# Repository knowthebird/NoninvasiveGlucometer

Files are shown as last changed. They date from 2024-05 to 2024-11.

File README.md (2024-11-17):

## Design and Build An Accurate Noninvasive Glucometer

### Table of Contents
1. [Overview](#overview)
2. [Example Sensors  (Glucosans)](#example-sensors-glucosans)
3. [Testing Notes](#testing-notes)
4. [Resources and References](#resources-and-references)

## Overview
This was originally to host a competition to design and build the most accurate noninvasive glucometer sensor.  Despite some interest, there were no entries.  Instead, now it currently just hosts my designs.  

The $1750 set aside for prizes will be kept available as a fund for anyone interested in developing a noninvasive glucometer sensor. If you have an idea for a design and want to chat about it or request some support, or if you are interested in refining these designs, reach out to noninvasiveglucometer@gmail.com

The motivation for the competition and designs is to increase the information available to the general public on noninvasive sensors by evaluating the accuracy of different sensor designs and to provide all the information needed to recreate those designs freely.  This is in the hopes that in the near future there may be an affordable sensor which can reliably provide accurate readings, and reduce the pain, cost, and waste associated with typical glucometers.
 
The information provided here has not been evaluated by the Food and Drug Administration.  The information provided here is not intended to diagnose, treat, cure, or prevent any disease.

Please feel free to reach out to noninvasiveglucometer@gmail.com with any questions, suggestions, comments, or concerns.

## Example Sensors (Glucosans)
This repository contains example "Glucosans" for reference. These are various designs to approach the problem, and the succeses and failures of them will be shared. 

**Glucosan**
 * **G**lucometer
 * **L**ightweight
 * **U**niversal
 * **C**ost-effective
 * **O**pen **S**ource
 * **A**ccurate
 * **N**oninvasive

| Overview | Glucosan 1 | Glucosan 2 |
| :--------- | :-------- | :------- |
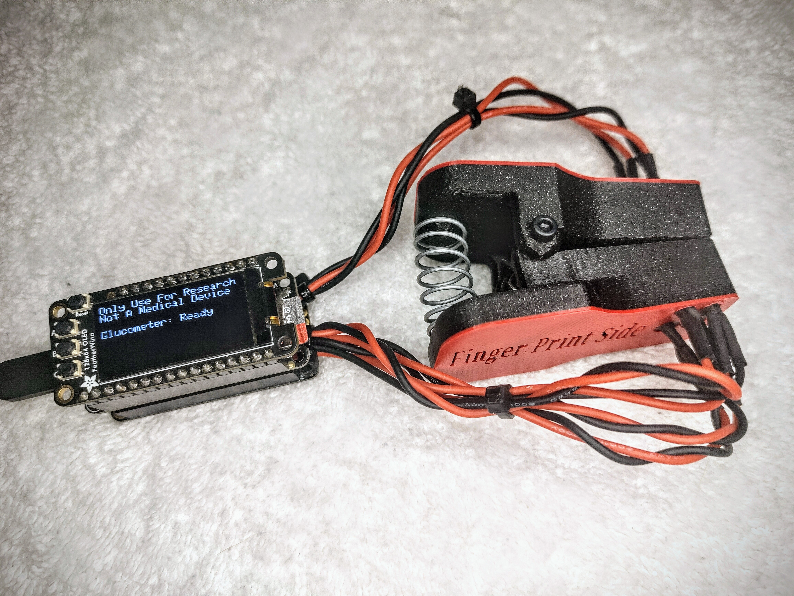
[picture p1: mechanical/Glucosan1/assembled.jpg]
| Image | | Coming Soon! |
| Method | IR Spectrometry | IR Spectrometry |
| Design | Done | In Progress |
| Build | Done | TODO |
| Log Data | 2 Persons, ~150 logs, 76-447mg/dl | TODO |
| Analysis Algorithims | External, Post Processing, Linear Regression | TODO |
| Correlations | Weak to None  | TODO |
| Emitters   | 1 x 617nm, 1 x 940nm | 1 x 670nm, 1 x 850nm, 1 x 950nm, 1 x 1300nm, 1 x 1550nm |
| Reflectance Detectors  | Phototransistors 1 x 630nm, 1 x 940nm (Si)  | None |
| Transmittance Detectors   | Phototransistors 1 x 630nm, 1 x 940nm (Si) | Photodiodes, 1 x 950nm (Si), 1 x 1650nm (InGaAs) |
| ADC | bypass caps, 12 bit resolution | analog front end IC, 14 bit resolution |
| Core Platform   | Adafruit Feather M0 Adalogger | Adafruit Feather RP2040 Adalogger |
| Display   | 128x64 OLED  | 128x64 OLED |
| SD Card   | CSV or Binary Logging | CSV or Binary Logging |
| Wireless   | None | None |
| IMU   | None  | 2 x Accel, 2 x Gyro |
| Temperature   | None  | 1 x Temp |
| Size   | TODO  | TODO |
| Weight   | TODO  | TODO |
| Power   | TODO  | TODO |
| Cost   | $48.33  | $188.31 |

## Testing Notes

<b>Nov 17, 2024:</b> Additional logs were taken with Glucosan 1 over a wide range of blood glucose levels. Looking closer at the log data showed what appeared to be corrupt signal readings, with a single sensor log showing multiple samples of the same photoplethysmogram (PPG) waveform slightly shifted. Because they were clearly shifted, but otherwise near identical signals representing the same PPG data, it does not look like an aliasing artifact from outside noise.  This can be seen looking at the readings from all sensors (regardless of LED state).  In some logs the corruption appears to "toggle" off and on, where the separation between duplicate signals widens.  My initial suspician is there is a hardware failure causing coupling between the sensors. It was not identified until reviewing a large set of samples. This should be kept in mind when referring to data from logs 85 to 174.  See log data folder for more details.

Initial tests with Glucosan 1 have showed weak to no correlation with blood glucose levels.  This is after gaining a wider range of data (see UserTwoLogData.csv) to verify outputs.  This may be due a few causes, including:
* Flexibility in the finger clamp was intended to allow a better seal on the finger from ambient light.  Distance of light source to sensor significantly affects readings.  Very possible changes in finger (emitter/sensor) positions are overshadowing any blood glucose levels changes detected by the sensor. Slightly moving the finger forward or backward in the clamp can almost immediatly exceed a .25V difference.  Possible solutions are puting the emitter and sensor in fixed positions where the clamp is not flexible, or including IMUs on the sensor and emitter such that the distance between the two can be calculated.
* Similarly, Nothing controlling movement, shaking, or vibrations when taking readings, or tracking them to filter against. A solution could be to use IMUs could monitor movement, or alert the user the device/finger is not stable enough to take a valid measurement. 
* Lack of environmental controls.  Glucosan 1 is portable and used in a variety of environments, and could be influenced by factors like various lighting. Possible solution is to always use in the same position for tests.

<b>July, 2024:</b> So far with Glucosan 1, only weak correlations have been observed.  This has relatively little significance at this point though, because it has only logged a very small amount of data with a relatively small range of blood glucose levels.  Getting a large set of samples, with a range in blood glucose levels, to both train and test models, is a challenge for any new sensor developemnt.  Without a range of data, initial results, such as MARD or RMSE, can be very misleading.
   * <b>YoutTube Video - Noninvasive Glucometer, Part 1, Initial Design Progress </b>
YoutTube Video, Noninvasive Glucometer, Part 1, Initial Design Progress (https://www.youtube.com/watch?v=Cop63ntB-sQ)

## Resources and References

1. Hina A, Saadeh W. Noninvasive Blood Glucose Monitoring Systems Using Near-Infrared Technology-A Review. Sensors (Basel). 2022 Jun 27;22(13):4855. doi: 10.3390/s22134855. PMID: 35808352; PMCID: PMC9268854.
   * https://www.mdpi.com/1424-8220/22/13/4855
2. Javid B, Fotouhi-Ghazvini F, Zakeri FS. Noninvasive Optical Diagnostic Techniques for Mobile Blood Glucose and Bilirubin Monitoring. J Med Signals Sens. 2018 Jul-Sep;8(3):125-139. doi: 10.4103/jmss.JMSS_8_18. PMID: 30181961; PMCID: PMC6116315.
   * https://pmc.ncbi.nlm.nih.gov/articles/PMC6116315/
3. Meter, G. (2015, August 27). Open Source Non-Invasive Glucose Meter - Expensive, Wasteful, and Annoying. YouTube
   * https://youtu.be/2np7Va2ASF0?si=skVRlG87lIETs9TL
4. Bhuyan, Muhibul. (2020). Design and Implementation of an NIR-Technique Based Non-Invasive Glucometer using Microcontroller. 20. 
   * https://tinyurl.com/j6b6d8wd
5. Beckers, I. (n.d.). Measuring glucose concentration nir absorption spectroscopy. Oxford Instruments. 
   * https://andor.oxinst.com/learning/view/article/spectral-response-of-glucose 
6. Naresh M, Nagaraju VS, Kollem S, Kumar J, Peddakrishna S. Non-invasive glucose prediction and classification using NIR technology with machine learning. Heliyon. 2024 Mar 28;10(7):e28720. doi: 10.1016/j.heliyon.2024.e28720. PMID: 38601525; PMCID: PMC11004754.
   * https://www.sciencedirect.com/science/article/pii/S2405844024047510

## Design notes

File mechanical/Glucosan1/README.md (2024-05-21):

FIngerClampBase.stl and FingerClampTop.stl modified from https://www.thingiverse.com/thing:2052975 by Drasko (https://www.thingiverse.com/drasko/designs). Original provided under the under the Creative Commons - Attribution license, CC BY, https://creativecommons.org/licenses/by/4.0/

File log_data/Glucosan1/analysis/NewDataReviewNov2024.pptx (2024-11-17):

## Noninvasive Glucometer

General Updates
Nov 2024
https://github.com/knowthebird/NoninvasiveGlucometer

## Contest Updates

- There were no contest entries
  - Prizes will be saved/used as fund for noninvasive glucometer projects
  - If you have an idea for a design and want to chat about it, or request some support, or if you are interested in refining the designs in the git repo, reach out to noninvasiveglucometer@gmail.com
- There were people who reached out with interest in how things were designed and suggestions for improvements in the future
- Just because there were not entries in the contest does not mean there is not interest in the problem
  - Many are going to look to protect their intellectual property, and not quickly share it for collaboration

## New Log Data

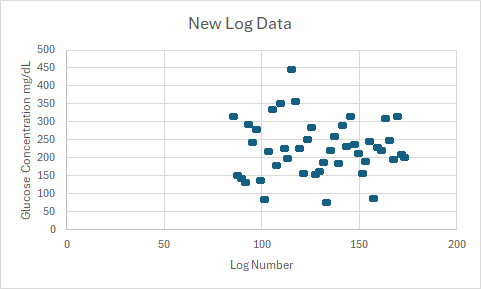
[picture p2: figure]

- Lots of new samples,
  - 89, two logs per session, separate fingers
  - A very wide range of concentration, 76 – 447 mg/dL
  - Thank you Dave!
- Expected results are:
  - As blood glucose concentration increases more light is absorbed by the glucose and both reflectance and transmittance sensors report less light
  - For this design, sensors report higher voltage when more light is absorbed
    - 12-bit resolution, 3V ~= 4096, 0V = 0
  - When looking at results, higher number should mean higher concentration
- This was not observed.
  - Even when looking at the same finger and same sensor, the general voltage does not follow the glucose concentration.

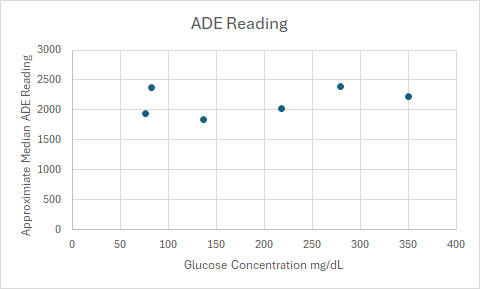
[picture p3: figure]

## Glucosan 1- Hardware Failure

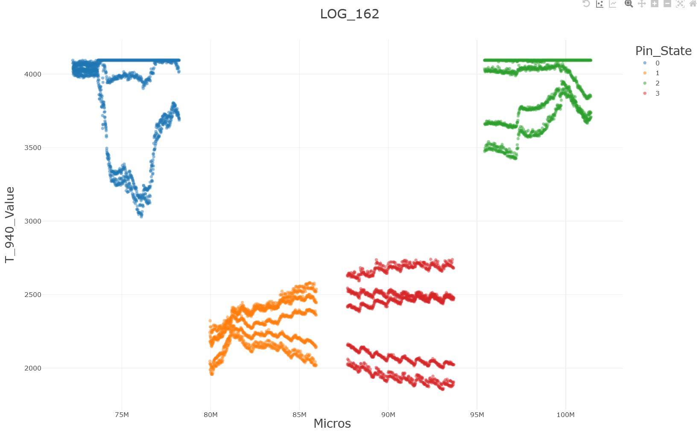
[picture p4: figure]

PPG Waveform appears to be
Duplicated in readings.

## Glucosan 1- Hardware Failure

Duplication appears to be present in
almost every log for 85-174. In some log
files it appeared to “toggle” off and on.
Note, there are not new software calls that
should be made during this “toggle”.

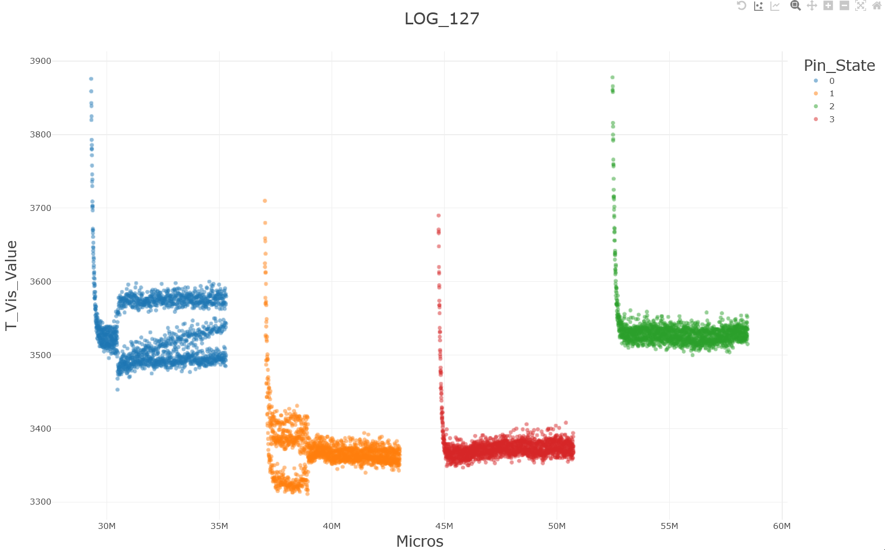
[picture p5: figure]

Signal appears to become duplicated .
Occurs in state where LEDs or all off.

Duplication appears to stop.
Occurs in state where one LEDs is on.

## Glucosan 1- Hardware Failure

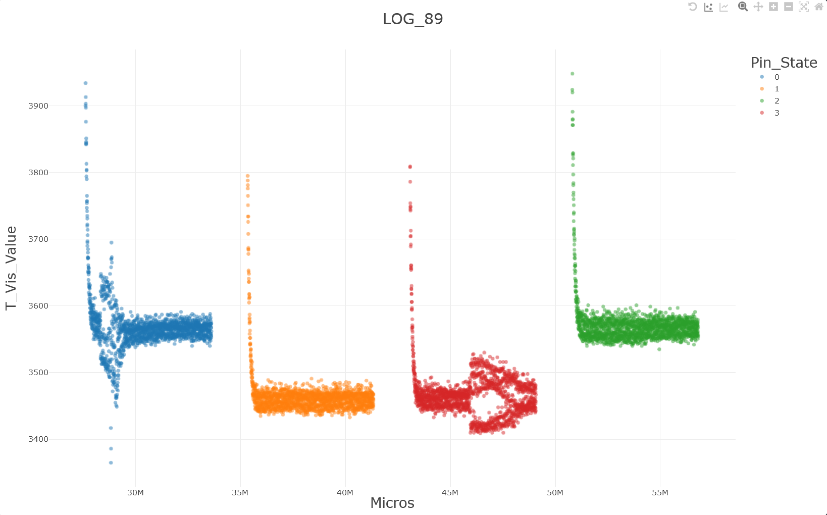
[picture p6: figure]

Even when less separated, there does appear
to be duplication or shifting occurring here.

Duplication becomes less seperated.
Occurs in state where LEDs or all off.

Duplication appears to widen again.
Occurs in state where two LEDs are on.

## Glucosan 1- Hardware Failure

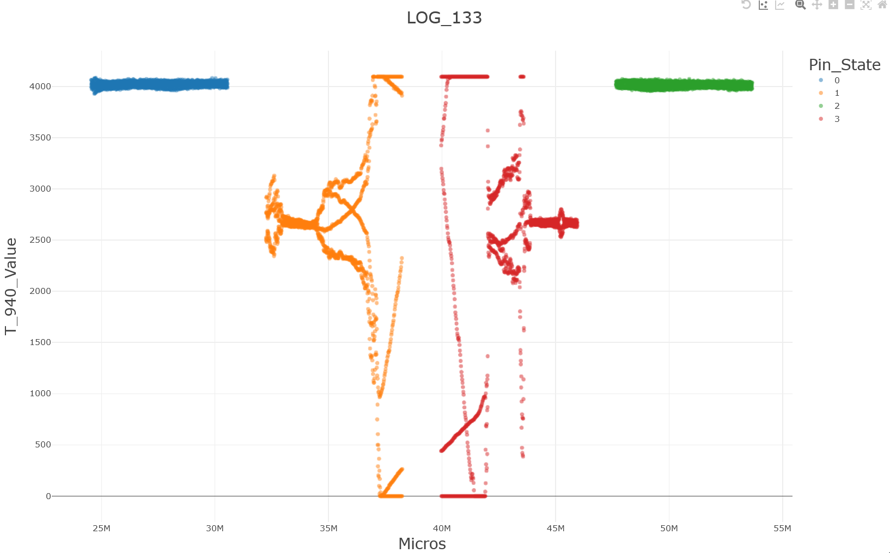
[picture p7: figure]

In some cases, the sensors appear to be completely failing.

## Movement Artifacts

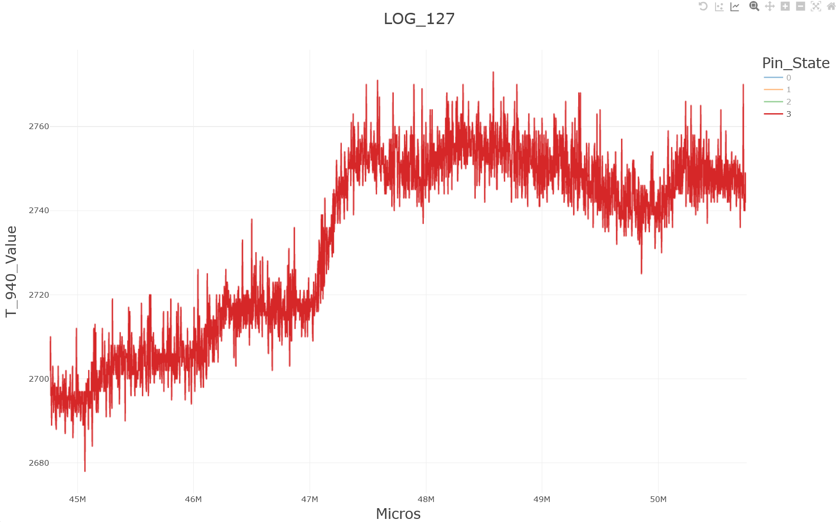
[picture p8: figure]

- Easy to see visually looking at logs but will require post processing algorithms to filter out.
- Currently no IMU to monitor for movement for post processing or to alert.

## In Hindsight – Lesson Learned

- Getting a variety of samples is not trivial
  - Glucose concentrations typically stays in a set range, and extremes are a health risk.
- Hardware needs to be more reliable before sending out in the world
- A way of sharing results remotely (ex: over wifi), could make it easier to remotely identify issues faster

## Short Term Next Steps – Simplify the Problem

- Measure Controlled Samples In A Controlled Environment
  - Cuvette containing solution of dextrose monohydrate in distilled water
  - Fixed position of emitters and sensors
    - Can 3D print a jig
  - PC Oscilloscope for Sampling Sensor
    - Built in Logging
      - No concerns of microcontroller wiring or logging corrupting sampling
    - High Sampling Rates
      - Will be more helpful when ready to monitor PPG waveforms
  - Test with probes and consider coverings to reduce noise in readings.

## Longer Term – Improvements For A Portable Device

- Fixed position for Sensor and Emitter
  - Makes problem less complex when not accounting for their movement
- IMUs on device and/or finger/ear
  - Need to be able to say what are artifacts of movement and be able to notify user of bad samples
- Maybe Cover the sensor and emitter
  - Maybe you a bag, glove, or cover of some kind to prevent noise on sensors
  - May be more important with a fixed sensor/emitter introducing air gaps
- Very long term, consider ability to share data through wifi or cell phone application
  - Could allow quicker results, and possibly a method for pushing updates back to the device
  - Adds complexity and data security risks too

## The Research and Development Is Active

- Companies
  - Abbott Laboratories
  - Apollon
  - Ascensia Diabetes Care Holdings AG
  - Biolinq Inc.
  - DexCom, Inc.
  - DiaMonTech AG
  - Glucosense Diagnostics
  - HagarTech
  - Integrity Applications, Inc.
  - Know Labs
  - LifePlusAI
  - LifeScan, Inc.
  - Medtronic plc
  - Movano, Inc.
  - Nemaura Medical
  - Profusa, Inc.
  - Roche Diagnostics
  - Scanbo
  - Senseonics Holdings, Inc.
  - RSP Systems
  - PK Vitality
  - Cnoga

Universities
Cardiff University
Kennesaw State University
Massachusetts Institute of Technology (MIT)
Monash University
National Taiwan Ocean University
RMIT University
Singapore National Population Health Survey
University of Chinese Academy of Sciences
University of Leeds
University of Missouri
Ulsan National Institute of Science and Technology (UNIST)

Lists provided by Amer Khaqan

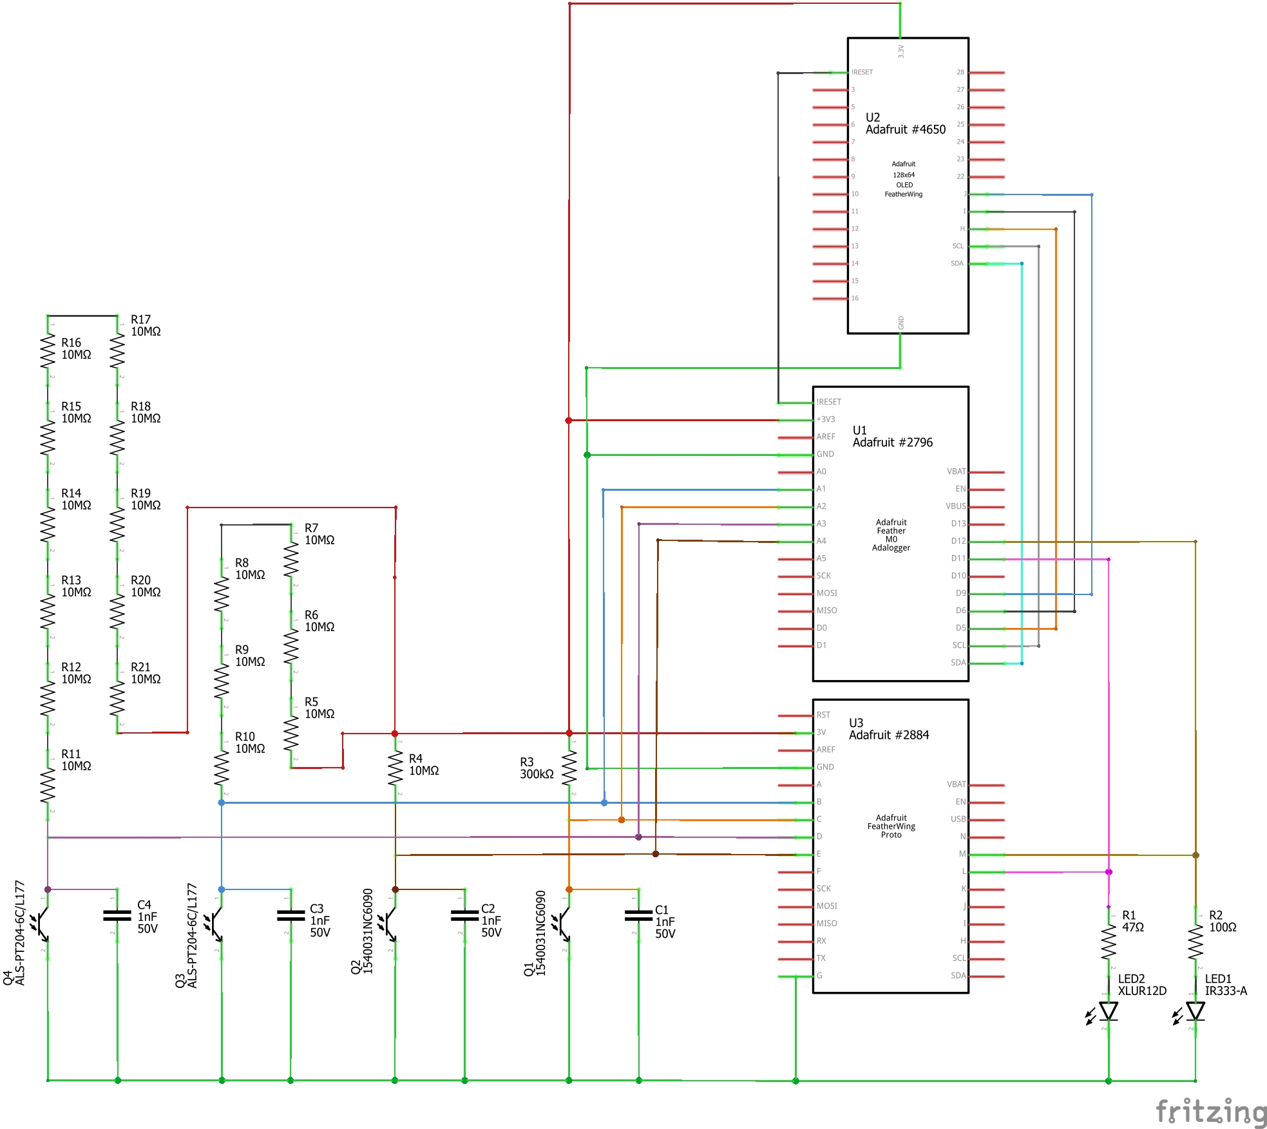
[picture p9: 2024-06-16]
electrical/Glucosan1/Schematic.jpg

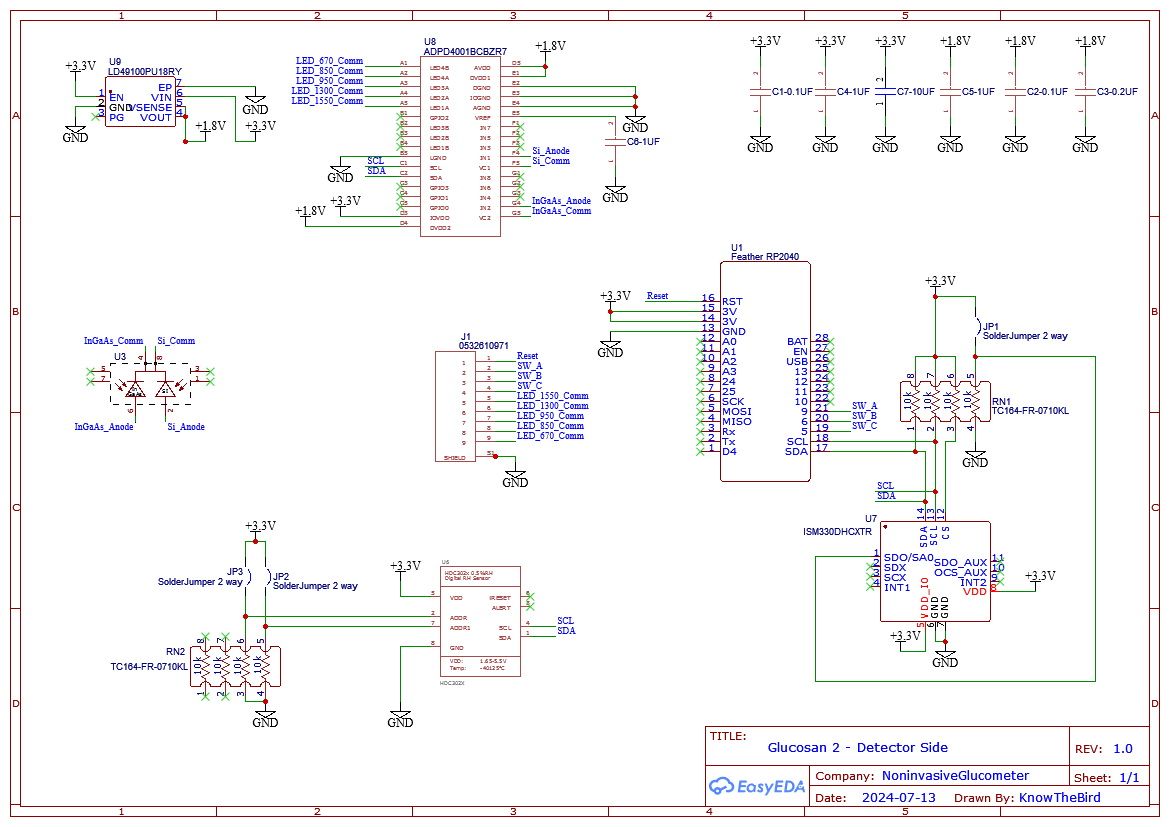
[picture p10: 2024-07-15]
electrical/Glucosan2/Schematic_Glucosan2-DetectorSide.png

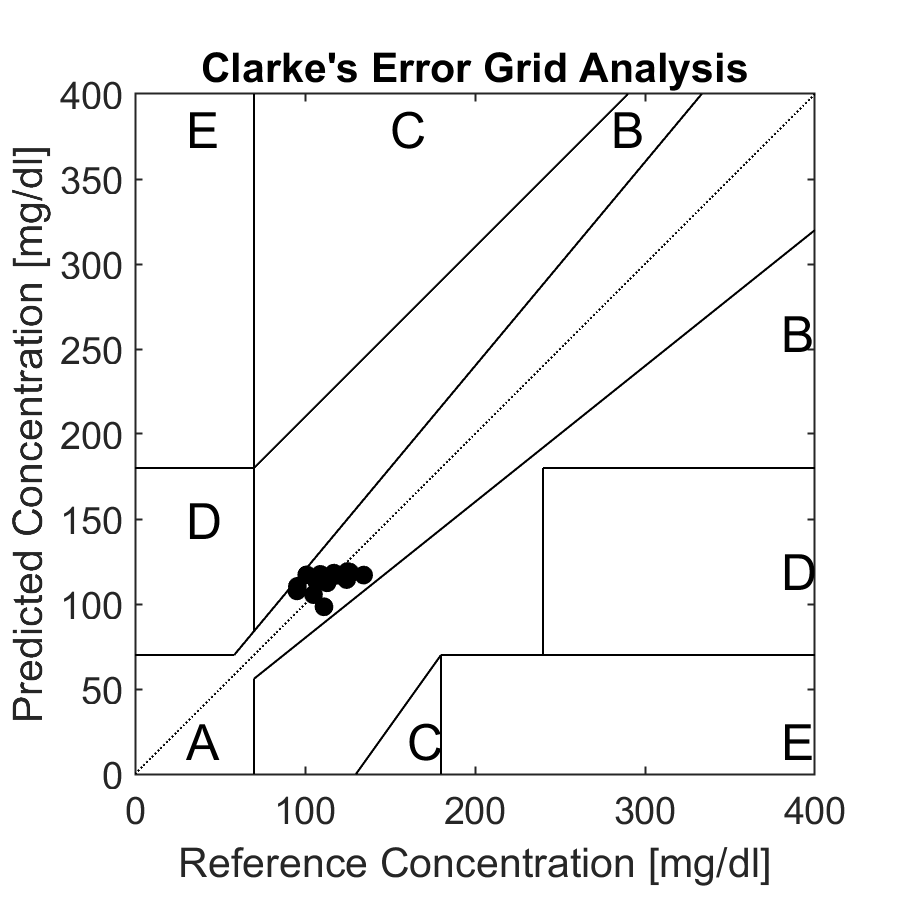
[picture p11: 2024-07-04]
log_data/Glucosan1/analysis/Clarke_EGA.png

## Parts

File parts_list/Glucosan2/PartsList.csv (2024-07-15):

Reference ID | Manufacturer or Supplier Part Number | Description | Manufacturer or Supplier | Quanity | Cost per Unit | Total Cost | Link
U1 | 5980 | Adafruit Feather RP2040 Adalogger | Adafruit | 1 | $14.95 | $14.95 | https://www.adafruit.com/product/5980
U2 | 4650 | FeatherWing 128x64 OLED | Adafruit | 1 | $14.95 | $14.95 | https://learn.adafruit.com/adafruit-128x64-oled-featherwing
U3 | MT03-047 | Photodiode 950/1650NM SMD | Marktech Optoelectronics | 1 | $55.36 | $55.36 | https://www.digikey.com/en/products/detail/marktech-optoelectronics/MT03-047/9954357
U4 | MTMD6891T38 | Emmiter IR MULTI-NM 100MA TO-5-8 | Marktech Optoelectronics | 1 | $40.68 | $40.68 | https://www.digikey.com/en/products/detail/marktech-optoelectronics/MTMD6891T38/4746379
U5 | MTE5115W-WRC | SWIR Emitter 1550NM TO-46 FLAT L | Marktech Optoelectronics | 1 | $15.32 | $15.32 | https://www.digikey.com/en/products/detail/marktech-optoelectronics/MTE5115W-WRC/9955415
U6 | HDC3021DEHR | Humidity Temperature Sensor Surface Mount I2C | Texas Instruments | 1 | $4.54 | $4.54 | https://www.digikey.com/en/products/detail/texas-instruments/HDC3021DEHR/17884945
U7 | ISM330DHCX | Accelerometer Gyroscope I2C | STmicroelectronics | 2 | $9.60 | $19.20 | https://www.st.com/en/mems-and-sensors/ism330dhcx.html#overview
U8 | ADPD4001BCBZR7 | Sensor Interface Multi-modal Optical AFE I2C | Analog Devices | 1 | $15.37 | $15.37 | https://www.mouser.com/ProductDetail/Analog-Devices/ADPD4001BCBZR7?qs=l4Gc20tDgJKpnSaEa3zOeQ%3D%3D
U9 | LD49100PU18RY | IC REG LINEAR 1.8V 1A 6DFN | STmicroelectronics | 1 | $1.61 | $1.61 | https://www.digikey.com/en/products/detail/stmicroelectronics/LD49100PU18RY/13175992
RN1 | TC164-FR-0710KL | 10k Resistor Array | Yageo | 2 | $0.14 | $0.28 | https://www.digikey.com/en/products/detail/yageo/TC164-FR-0710KL/5950695
C1-C3 | GCJ188R71E104KA12D | Capacitor ceramic 0.1uF 0603 | Murata Electronics | 3 | $0.17 | $0.51 | https://www.digikey.com/en/products/detail/murata-electronics/GCJ188R71E104KA12D/7363221
C4-C6 | GCJ188R71E105KA01D | Capacitor ceramic 1uF 0603 | Murata Electronics | 3 | $0.27 | $0.81 | https://www.digikey.com/en/products/detail/murata-electronics/GCJ188R71E105KA01D/6606038
C7 | CGA4J1X7S1E106K125AE | Capacitor ceramic 10uF 0805 | TDK Corporation | 1 | $0.73 | $0.73 | https://www.digikey.com/en/products/detail/tdk-corporation/CGA4J1X7S1E106K125AE/9744777
S1 | 2940 | 12-pin and 16-pin Female Header Set Short | Adafruit | 2 | $1.50 | $3.00 | https://www.adafruit.com/product/2940
S2 | 3002 | 12-pin and 16-pin Male Header Set Short | Adafruit | 2 | $0.50 | $1.00 | https://www.adafruit.com/product/3002
S3 | 532610971 | Connector Header SMD Right Angle 9 Pos PicoBlade | Molex | 2 | $1.01 | $2.02 | https://www.digikey.com/en/products/detail/molex/0532610971/699101
NA | 3096525-M | Wire Solder 180 C | MULTICORE / LOCTITE | As Needed | NA | NA | https://www.amazon.com/gp/product/B00DKF13JY/ref=ppx_yo_dt_b_search_asin_title?ie=UTF8&psc=1
 |  | Total |  |  |  | $190.33

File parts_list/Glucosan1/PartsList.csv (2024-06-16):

Reference ID | Manufacturer or Supplier Part Number | Description | Manufacturer or Supplier | Quanity | Cost per Unit | Total Cost | Link
U1 | 2796 | Adafruit Feather M0 Adalogger | Adafruit | 1 | $19.95 | $19.95 | https://learn.adafruit.com/adafruit-feather-m0-adalogger
U2 | 4650 | FeatherWing 128x64 OLED | Adafruit | 1 | $14.95 | $14.95 | https://learn.adafruit.com/adafruit-128x64-oled-featherwing
U3 | 2884 | FeatherWing Proto | Adafruit | 1 | $4.95 | $4.95 | https://www.adafruit.com/product/2884
P1 | 2830 | 12-pin and 16-pin Stacking Headers | Adafruit | 1 | $1.25 | $1.25 | https://www.adafruit.com/product/2830
S1 | 2886 | 12-pin and 16-pin Female Header Set | Adafruit | 1 | $0.95 | $0.95 | https://www.adafruit.com/product/2886
Q1-Q2 | 1540031NC6090 | Phototransistors 940nm | Würth Elektronik | 2 | $0.44 | $0.88 | https://www.digikey.com/en/products/detail/w%C3%BCrth-elektronik/1540031NC6090/12366941
Q3-Q4 | ALS-PT204-6C/L177 | Phototransistors 630nm Radial | Everlight Electronics Co Ltd | 2 | $0.62 | $1.24 | https://www.digikey.com/en/products/detail/everlight-electronics-co-ltd/ALS-PT204-6C-L177/2675510
LED1 | IR333-A | EMITTER IR 940NM 100MA RADIAL | Everlight Electronics Co Ltd | 1 | $0.53 | $0.53 | https://www.digikey.com/en/products/detail/everlight-electronics-co-ltd/IR333-A/2675571
LED2 | XLUR12D | Red 617nm LED Indication | SunLED | 1 | $0.28 | $0.28 | https://www.digikey.com/en/products/detail/sunled/XLUR12D/4745846
R1 | CF14JT47R0 | Resistor 47 Ohm 1/4 Watt 5% Tolerance Through Hole | Stackpole Electronics Inc | 1 | $0.10 | $0.10 | https://www.digikey.com/en/products/detail/stackpole-electronics-inc/CF14JT47R0/1741438
R2 | CF14JT100R | Resistor 100 Ohm 1/4 Watt 5% Tolerance Through Hole | Stackpole Electronics Inc | 1 | $0.10 | $0.10 | https://www.digikey.com/en/products/detail/stackpole-electronics-inc/CF14JT100R/1741261
R3 | CF14JT300K | Resistor 300k Ohm 1/4 Watt 5% Tolerance Through Hole | Stackpole Electronics Inc | 1 | $0.10 | $0.10 | https://www.digikey.com/en/products/detail/stackpole-electronics-inc/CF14JT300K/1741393
R4-R21 | An-resistor01 | Resistor 10M Ohm 1/4 Watt 1% Tolerance Through Hole | Aniann | 18 | $0.01 | $0.18 | https://www.amazon.com/dp/B07L851T3V?psc=1&ref=ppx_yo2ov_dt_b_product_details
C1-C4 | EE916A | Capacitor 1nF Ceramic 50V Radial Lead | 1A Manufacturing Ltd. | 4 | $0.10 | $0.40 | https://www.amazon.com/dp/B094HRK8QX?ref=ppx_yo2ov_dt_b_product_details&th=1
SPR1 | 540278 | Spring Compression #93 1.125" long 0.5"od .287mm solid height 5lbs per in | HILLMAN | 1 | $1.99 | $1.99 | https://shop.hillmangroup.com/ccrz__ProductDetails?sku=540278&cclcl=en_US/1000
CS1-CS2 | 91290A120 | Screw M3 x 16mm Socket Head Steel Black Oxide | McMASTER | 2 | $0.12 | $0.24 | https://www.mcmaster.com/91290A120/
HN1-HN2 | 90593A001 | Nut M3 Hex Steel Black Oxide | McMASTER | 2 | $0.12 | $0.24 | https://www.mcmaster.com/90593A001/
NA | 22GA | 22 AWG Stranded Wire Kit (multicolor) Silicone Coated | WiderCable | As Needed | NA | NA | https://www.amazon.com/gp/product/B07T4SYVYG/ref=ppx_yo_dt_b_search_asin_title?ie=UTF8&th=1
NA | 3096525-M | Wire Solder 180 C | MULTICORE / LOCTITE | As Needed | NA | NA | https://www.amazon.com/gp/product/B00DKF13JY/ref=ppx_yo_dt_b_search_asin_title?ie=UTF8&psc=1
NA | MP-H002-04-156 | Heat Shrink Tubing Kit Assorted Sizes | MILAPEAK | As Needed | NA | NA | https://www.amazon.com/gp/product/B07QM8249H/ref=ppx_yo_dt_b_search_asin_title?ie=UTF8&psc=1
NA | 4+6+8+12 (400 Pack) | Wire Ties Assorted Sizes UV Resistant | ANOSON | As Needed | NA | NA | https://www.amazon.com/gp/product/B0C2Z4L3S6/ref=ppx_yo_dt_b_search_asin_title?ie=UTF8&th=1
 |  | Total |  |  |  | $48.33

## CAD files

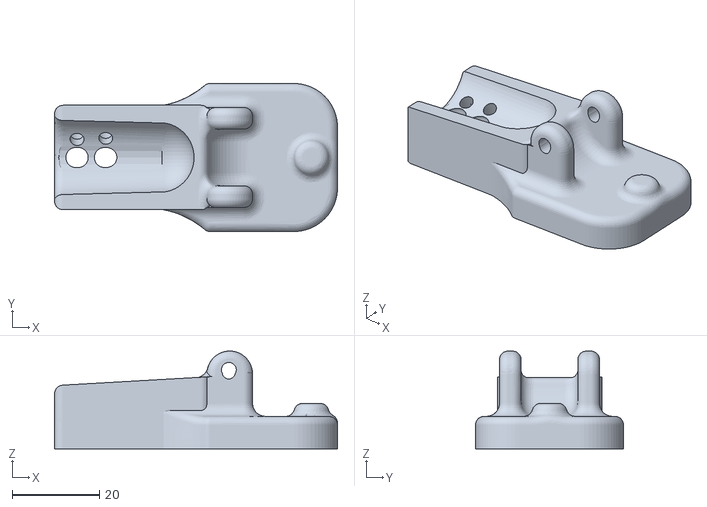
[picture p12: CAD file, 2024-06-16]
mechanical/Glucosan1/FingerClampPrintSide.stl
65.0 x 34.0 x 22.5

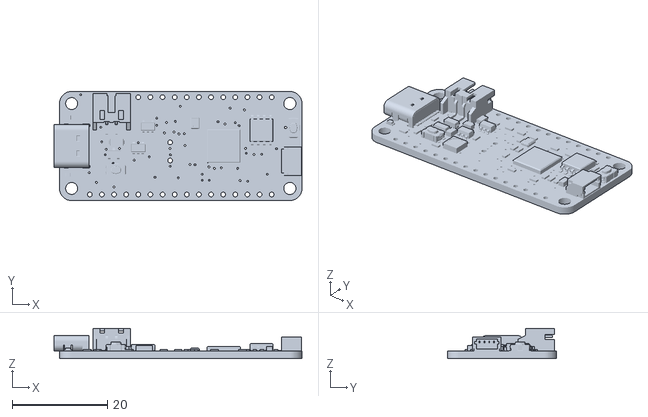
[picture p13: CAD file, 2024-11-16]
mechanical/Glucosan2/4884 Feather RP2040.stl
51.9 x 22.9 x 6.37

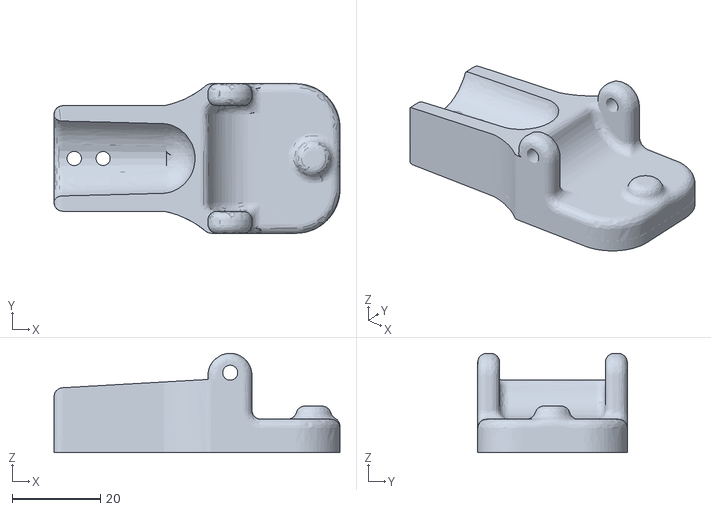
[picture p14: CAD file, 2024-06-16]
mechanical/Glucosan1/FingerClampNailSide.stl
65.0 x 34.0 x 22.6

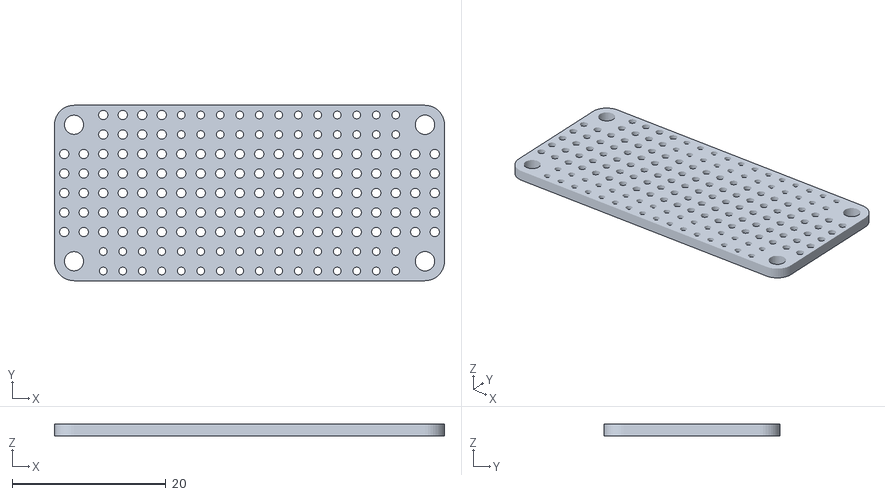
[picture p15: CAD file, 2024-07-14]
mechanical/Glucosan2/2884 Proto FeatherWing.stl
50.8 x 22.9 x 1.57

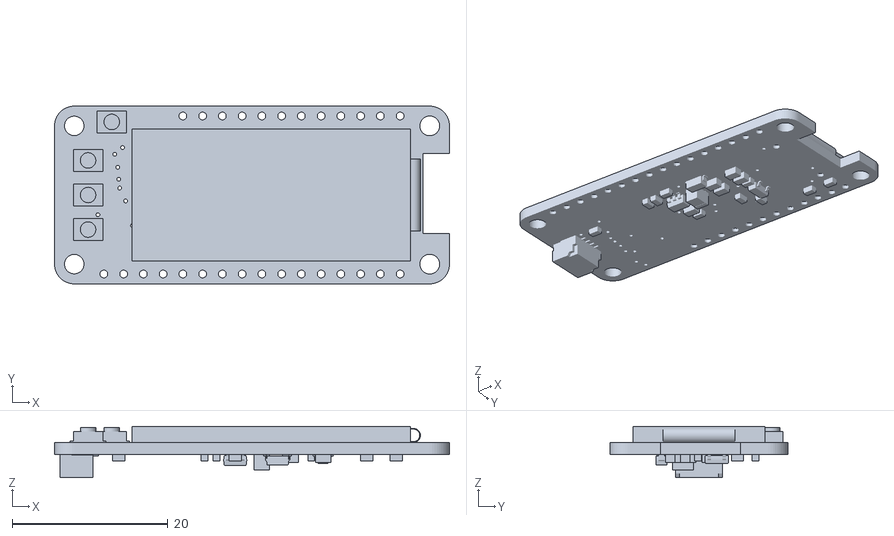
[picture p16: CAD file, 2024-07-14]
mechanical/Glucosan2/4650 OLED FeatherWing.stl
50.8 x 22.9 x 6.59

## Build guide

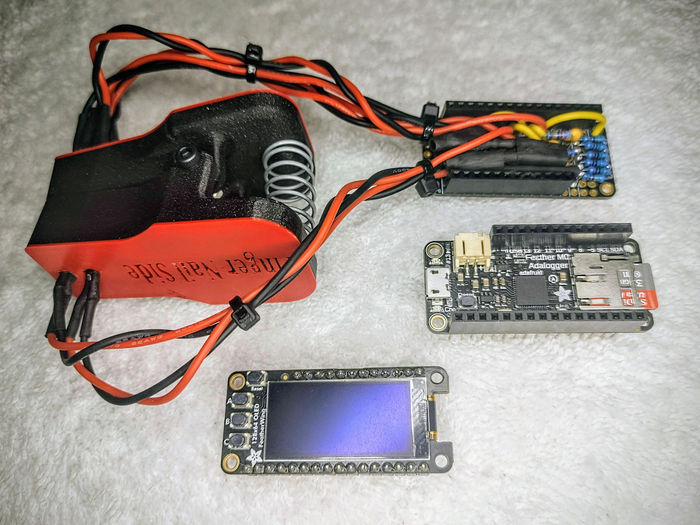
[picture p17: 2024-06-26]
mechanical/Glucosan1/disassembled.jpg

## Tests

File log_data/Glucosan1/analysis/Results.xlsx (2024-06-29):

PreLog BG, All LED Values | R_940_Value | R_Vis_Value | T_940_Value | T_Vis_Value | PreLog BG, Index Finger | R_940_Value | R_Vis_Value | T_940_Value | T_Vis_Value
IndexFinger | 0.0073 | 0.0104 | 0.2019 | 0.093 | LEDs Off | 0.0904 | 0.1315 | 0.2364 | 0.1498
IndexFingerNail | -0.0071 | -0.0349 | 0.0952 | 0.0137 | IR On | 0.1656 | 0.1961 | 0.259 | 0.1695
PinkyFinger | -0.0043 | -0.0174 | 0.1451 | 0.0957 | Vis On | 0.0911 | -0.3036 | 0.2266 | 0.1079
PinkyFingerNail | -0.0196 | -0.0669 | 0.148 | 0.0037 | Both On | 0.1663 | 0.0499 | 0.2518 | 0.1267
MeanLog BG, All LED Values | R_940_Value | R_Vis_Value | T_940_Value | T_Vis_Value | MeanLog BG, Index Finger | R_940_Value | R_Vis_Value | T_940_Value | T_Vis_Value
IndexFinger | 0.0047 | 0.0069 | 0.2201 | 0.1018 | LEDs Off | 0.0975 | 0.0928 | 0.258 | 0.1539
IndexFingerNail | -0.0038 | -0.0271 | 0.12 | 0.0346 | IR On | 0.089 | 0.1269 | 0.2771 | 0.1703
PinkyFinger | -0.0068 | -0.0186 | 0.1744 | 0.1088 | Vis On | 0.0971 | -0.2426 | 0.2486 | 0.1261
PinkyFingerNail | -0.0168 | -0.0615 | 0.1881 | 0.0309 | Both On | 0.1152 | 0.0458 | 0.2778 | 0.1576
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

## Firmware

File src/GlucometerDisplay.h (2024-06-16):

#ifndef GLUCOMETERDISPLAY_H_
#define GLUCOMETERDISPLAY_H_

#include <Adafruit_GFX.h>
#include <Adafruit_SH110X.h>
#include <SPI.h>
#include <Wire.h>

#define kBUTTON_A 9
#define kBUTTON_B 6
#define kBUTTON_C 5

class Button {
 public:
  Button(const uint8_t k_button_pin,
         const uint8_t k_button_mode = INPUT,
         const unsigned long k_debounce_delay_ms = 60)
      : k_button_pin_(k_button_pin),
        k_button_mode_(k_button_mode),
        k_debounce_delay_ms_(k_debounce_delay_ms),
        last_button_state_(0),
        last_debounce_time_ms_(0) {}

  void Initialize() { pinMode(k_button_pin_, k_button_mode_); }

  uint8_t IsPressed() {
    uint8_t reading = digitalRead(k_button_pin_);

    if (k_button_mode_ == INPUT_PULLUP) {
      reading = !reading;
    }

    if (reading != last_button_state_) {
      last_debounce_time_ms_ = millis();
    }

    if ((millis() - last_debounce_time_ms_) > k_debounce_delay_ms_) {
      button_state_ = reading;
    }

    last_button_state_ = reading;
    return button_state_;
  }

  uint8_t IsNewPress() {
    uint8_t prev_state = button_state_;
    IsPressed();
    return ((prev_state != button_state_) && (button_state_));
  }

  virtual ~Button() {}

 private:
  const uint8_t k_button_pin_;
  const uint8_t k_button_mode_;
  const unsigned long k_debounce_delay_ms_;  // the debounce time; increase if
                                             // the output flickers
  uint8_t button_state_;       // the current reading from the input pin
  uint8_t last_button_state_;  // the previous reading from the input pin
  unsigned long
      last_debounce_time_ms_;  // the last time the output pin was toggled
};

class GlucometerDisplay {
 public:
  GlucometerDisplay()
      : read_button_(kBUTTON_A, INPUT_PULLUP),
        log_sd_button_(kBUTTON_B, INPUT_PULLUP),
        stream_serial_button_(kBUTTON_C, INPUT_PULLUP),
        display_(Adafruit_SH1107(64, 128, &Wire)) {}

  uint8_t Initialize() {
    delay(250);                  // wait for the OLED to power up
    display_.begin(0x3C, true);  // Address 0x3C default
    display_.setRotation(1);
    display_.setTextSize(1);
    display_.setTextColor(SH110X_WHITE);

    read_button_.Initialize();
    log_sd_button_.Initialize();
    stream_serial_button_.Initialize();
    return 0;
  }

  void PrintMsg(const char* msg) {
    ResetDisplay();
    display_.println(msg);
    display_.display();
  }

  void PrintConcentration_mg_dl(float reading) {
    ResetDisplay();
    display_.println("Done Reading");
    display_.print(reading);
    display_.println(" mg/dl");
    display_.print(reading / k_mg_dl_per_mmol_L_);
    display_.println(" mmol/L");
    display_.display();
  }

  virtual ~GlucometerDisplay() {}

  Button read_button_;
  Button log_sd_button_;
  Button stream_serial_button_;

 private:
  Adafruit_SH1107 display_;
  const float k_mg_dl_per_mmol_L_ = 18.0156;

  void ResetDisplay() {
    display_.clearDisplay();
    display_.setCursor(0, 0);
    display_.println("Only Use For Research");
    display_.println("Not A Medical Device");
    display_.println("");
  }
};

#endif  // GLUCOMETERDISPLAY_H_

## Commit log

2024-05-07 Begin adding a logger
    [PartsList.csv]
2024-05-08 Refactor with abstract class, reorganize files
    [PartsList.csv, bottom.stl, top.stl]
2024-05-10 Add IO for example sensor
2024-05-19 Add competition info
    [FingerClampBase.stl, FingerClampTop.stl, PartsList.csv, Schematic.fzz]
2024-05-19 Add method to position sensor
    [PartsList.csv, Schematic.fzz]
2024-05-19 Update spelling
    [FingerClampBase.stl, FingerClampTop.stl]
2024-05-21 Add finger clamp
    [FingerClampBase.stl, FingerClampTop.stl]
2024-05-27 Update resistor values and evaluation criteria
    [Schematic.fzz]
2024-05-27 Updates parts list and schematic
    [PartsList.csv, Schematic.fzz]
2024-06-16 New wiring, finger clamp, and logging
    [FingerClampBase.stl, FingerClampNailSide.stl, FingerClampPrintSide.stl, FingerClampTop.stl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]
2024-06-16 Correct schematic
    [Schematic.fzz]
2024-06-26 Add example sensor logs and images
    [Index.csv, LOG_1.CSV, LOG_10.CSV, LOG_11.CSV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]
2024-06-29 Update log data
    [Index.csv, LOG_1.CSV, LOG_10.CSV, LOG_11.CSV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]
2024-07-04 Reorganize log data
    [Index.csv, Results.xlsx]
2024-07-13 Update readme and example names
    [FingerClampNailSide.stl, FingerClampPrintSide.stl, Index.csv, PartsList.csv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]
2024-07-14 Begin PCB
    [2884 Proto FeatherWing.stl, 4650 OLED FeatherWing.stl, PartsList.csv]
2024-07-15 Update schematic for glucosan 2
    [PartsList.csv]
2024-11-16 Updates to readme, new log data
    [4884 Feather RP2040.stl]
